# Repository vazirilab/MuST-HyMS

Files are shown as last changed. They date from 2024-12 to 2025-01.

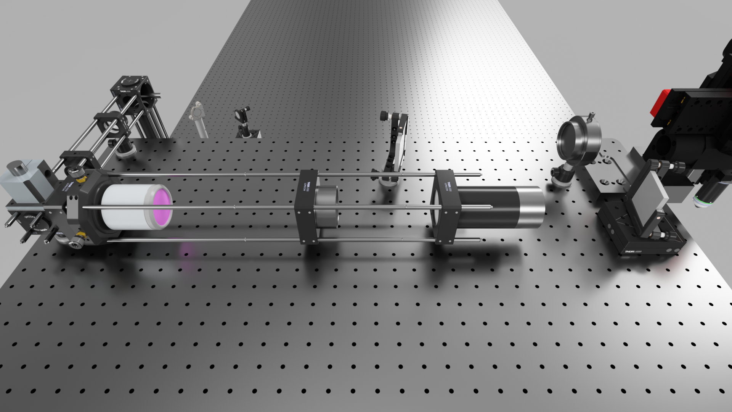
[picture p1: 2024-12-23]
Mechanical/03_3p-path_table-and-pltfrm/MuST_assembly_3p_v1_2017-Feb-16_03-30-20PM-000_CustomizedView4601048668.png

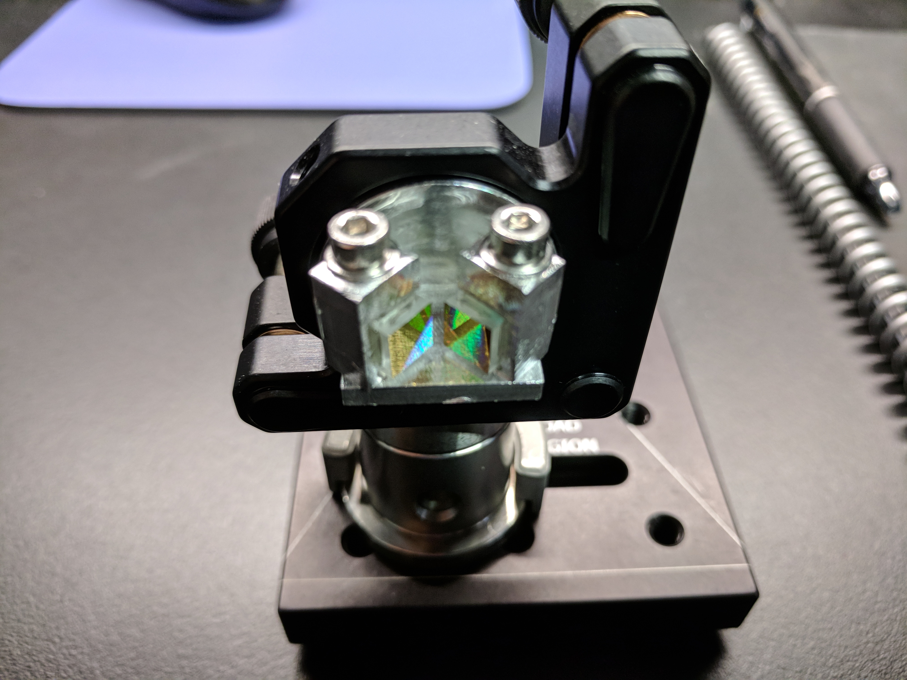
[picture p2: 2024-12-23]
Docs_Photos/HyMS_setup_photos/IMG_20180208_113904.jpg

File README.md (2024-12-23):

# Muliplexed Scanned Temporal Focusing (MuST) and Hybrid Multiplexed Sculpted Light (HyMS) Microscopy

This repository contains mechanical designs, parts lists, processing code, manuals, photos and other resources that enable users skilled in optical and mechanical lab techniques to build the MuST / HyMS microscope as published in the following peer-reviewed article:

Weisenburger, S., Tejera, F., Demas, J., Chen, B., Manley, J., Sparks, F. T., Martínez Traub, F., Daigle, T., Zeng, H., Losonczy, A. & Vaziri, A. 
Volumetric Ca<sup>2+</sup> Imaging in the Mouse Brain Using Hybrid Multiplexed Sculpted Light Microscopy. Cell 177, 1050-1066.e14 (2019). [doi:10.1016/j.cell.2019.03.011](https://doi.org/10.1016/j.cell.2019.03.011).

#### System requirements of the [MuST / HyMS processing pipeline](Code/)
- MATLAB Base
- MATLAB Parallel Computing Toolbox
- MATLAB Image Processing Toolbox
- MATLAB Statistics and Machine Learning Toolbox
- [ScanImageTiffReader](https://vidriotech.gitlab.io/scanimage-tiff-reader/)
- [NoRMCorre](https://github.com/flatironinstitute/NoRMCorre)
- [CaImAn-MATLAB](https://github.com/flatironinstitute/CaImAn-MATLAB)
- Tested with MATLAB R2017b on Red Hat Enterprise Linux 7.2

For additional information, please refer to the [Scan-TeFo / MuST / HyMS dissemination wiki](https://scantefo.rockefeller.edu/index.php?title=Main_Page).

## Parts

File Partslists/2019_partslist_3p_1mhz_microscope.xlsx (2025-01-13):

Parts | Vendor | Description | Part number | Qty
Laser | Class-5 | Class-5, OPCPA, 1300 nm, 1 MHz | WD
HWP | Thorlab | WPMH05M-1310 - Ø1/2" Mounted Multi-Order Half-Wave Plate, Ø1" Mount, 1310 nm | WPMH05M-1310 | 1
PBS | Thorlab | PBS123 - 1/2" Polarizing Beamsplitter Cube, 900 - 1300 nm | PBS123 | 1
L1 | Thorlab | Ø1" N-BK7 Plano-Convex Lens, SM1-Threaded Mount, f = 150 mm, ARC: 1050-1700 nm | LA1433-C-ML | 1
L2 | Thorlab | N-BK7 Plano-Concave Lens, Ø25 mm, f = -75 mm, AR Coating: 1050-1700 nm | LC1258-C | 1
EOM | Conoptics | Electro optic modulator Model 360-80 | 360-80 | 1
P1,P2 | Newport | Brewster Angle Dispersing Prism, Ultrafast, SF10, 25 mm, 370-2000 nm | 10SF10 | 2
Md | Thorlab | PFD10-03-P01 - Ø1" Protected Silver D-Shaped Mirror | PFD10-03-P01 | 1
M1 | Thorlab | PFSQ20-03-P01 - 2" x 2" Protected Silver Mirror | PFSQ20-03 | 1
M | Thorlab | PF10-03-P01 - Ø1" Protected Silver Mirror | PF10-03-P01 | 5
BS | Thorlab | Ø1/2" UVFS Beam Sampler for Beam Pick-Off, ARC: 1050-1700 nm, 3 mm Thick | BSF05-C | 1
PD | Thorlab | InGaAs Switchable Gain Amplified Detector, 800 - 1700 nm, 10 MHz BW, 3.14 mm2, M4 Taps | PDA20CS-EC | 1
L3,L4 | Thorlab | Mounted N-BK7 Bi-Convex Lens, Ø1", f = 125.0 mm, ARC: 1050 - 1700 nm | LB1904-C-ML | 2
L5, L6 | Thorlab | N-BK7 Plano-Convex Lens, Ø1", f = 100 mm, AR Coating: 1050 - 1700 nm | LA1509-C | 2
Rx | EOPC | 3 mm resonance scanner, 16 KHz | SC30 | 1
GX,Gy | Cambridge Tech | 5 mm Galvo scanner X and Y | 6215H | 1
SL | Thorlab | LSM05 - Scan Lens, 1250 to 1380 nm, EFL=110 mm | LSM05 | 1
S | Thorlab | SH1/M - Optical Beam Shutter with 10' Long Cable, Ø1" Aperture, Metric | SH1/M | 1
TL | Edmund Optics | f 400 mm achromactic lens |  | 1
OL | Nikon | Nikon 16x, 0.8 NA, 3 mm WD | CFI75LWD16xW2 | 1
Microscope Head | Sutter | Three axis movable objective microscope, 21.5 mm travel range | MP285 | 1
Microscope Optics | Semrock | 735 nm long pass dichroic mirror, 25 x 36 mm | FF735-Di02-25x36 | 1
 | Chroma | 575 nm longpass filter | 565DCXR | 1
 | Chroma | 605 nm bandpass filter | ET605/70m | 1
 | Chroma | 525 nm bandpass filter | ET525/70m | 1
PMT | Hamamatsu | Hamamatsu PMTs. GaAsP photocathode | H10770PA-40 | 2

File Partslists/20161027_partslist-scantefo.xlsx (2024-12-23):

Category | Purpose | Vendor | Part Number | Item | Product URL | Qty | Price | Subtotal | Currency | Order? | Arrived?
Multiplexing | 2x multiplexing | Thorlabs | PBS103 | 10 mm Polarizing Beamsplitter Cube 900 - 1300 nm | http://www.thorlabs.com/newgrouppage9.cfm?objectgroup_id=739 | 2 | $164.70 | $329.40 | USD | order by 30/05/2016 | YES
Multiplexing | 2x multiplexing | Thorlabs | AHWP05M-980 | Ø1/2" Mounted Achromatic Half-Wave Plate Ø1" Mount 690 - 1200 nm | http://www.thorlabs.com/newgrouppage9.cfm?objectgroup_id=854 | 1 | $704.70 | $704.70 | USD | order by 30/05/2016 | YES
Multiplexing | 2x multiplexing | Thorlabs | RSP1/M | Rotation Mount for Ø1" (25.4 mm) Optics M4 Tap | http://www.thorlabs.com/newgrouppage9.cfm?objectgroup_id=246 | 1 | $74.45 | $74.45 | USD | order by 30/05/2016 | YES
Multiplexing | 2x multiplexing | Thorlabs | MRA10-E03 | Right-Angle Prism Dielectric Mirror 750 - 1100 nm L = 10.0 mm | http://www.thorlabs.com/newgrouppage9.cfm?objectgroup_id=7715 | 1 | $94.50 | $94.50 | USD | order by 30/05/2016 | YES
Multiplexing | 2x multiplexing | Thorlabs | KM200S | Kinematic Mount for 2" (50.8 mm) Tall Rectangular Optics Right Handed | http://www.thorlabs.com/newgrouppage9.cfm?objectgroup_id=3971 | 2 | $119.70 | $239.40 | USD | order by 30/05/2016 | YES
Multiplexing | 2x multiplexing | Thorlabs | BBSQ2-E03 | 2" x 2" Square Broadband Dielectric Mirror 750 - 1100 nm | http://www.thorlabs.com/newgrouppage9.cfm?objectgroup_id=139 | 2 | $146.52 | $293.04 | USD | order by 30/05/2016 | YES
Multiplexing | 2x multiplexing | Thorlabs | PFD10-03-P01 | 1" Protected Silver D-Shaped Mirror | http://www.thorlabs.com/newgrouppage9.cfm?objectgroup_id=2632 | 2 | $49.50 | $99.00 | USD | order by 30/05/2016 | YES
Multiplexing | 2x multiplexing | Thorlabs | KM100D | Right-Handed Kinematic Mount for Ø1" D-Shaped Mirrors | http://www.thorlabs.com/newgrouppage9.cfm?objectgroup_id=2700 | 1 | $68.13 | $68.13 | USD | order by 30/05/2016 | YES
Multiplexing | 2x multiplexing | Thorlabs | BS011 | 50:50 Non-Polarizing Beamsplitter Cube 700-1100 nm 10 mm | http://www.thorlabs.com/newgrouppage9.cfm?objectgroup_id=6207 | 2 | $152.10 | $304.20 | USD | order by 30/05/2016 | YES
Multiplexing | 2x multiplexing | Thorlabs | MT1/M | 13 mm Translation Stage with Standard Micrometer M6 Taps | http://www.thorlabs.com/newgrouppage9.cfm?objectgroup_id=1908 | 2 | $257.40 | $514.80 | USD | order by 30/05/2016 | YES
Multiplexing | 2x multiplexing | Thorlabs | LMR3/M | Lens Mount with Retaining Ring for Ø3" Optics M4 Tap | http://www.thorlabs.com/newgrouppage9.cfm?objectgroup_id=1433 | 1 | $46.31 | $46.31 | USD | order by 30/05/2016 | YES
Multiplexing | 2x multiplexing | Thorlabs | KM100PM/M | 25 mm Kinematic Prism Mount M4 Taps | http://www.thorlabs.com/newgrouppage9.cfm?objectgroup_id=1811 | 5 | $65.25 | $326.25 | USD | order by 30/05/2016 | YES
Multiplexing | 2x multiplexing | Thorlabs | TR75/M | Ø12.7 mm Optical Post SS M4 Setscrew M6 Tap L = 75 mm | http://www.thorlabs.com/newgrouppage9.cfm?objectgroup_id=1266 | 7 | $4.88 | $34.16 | USD | order by 30/05/2016 | YES
Multiplexing | 2x multiplexing | Thorlabs | UPH75/M | Ø12.7 mm Universal Post Holder Spring-Loaded Locking Thumbscrew L = 75 mm | http://www.thorlabs.com/newgrouppage9.cfm?objectgroup_id=1982 | 7 | $27.54 | $192.78 | USD | order by 30/05/2016 | YES
Multiplexing | 2x multiplexing | Thorlabs | ID25/M | Mounted Standard Iris 25 mm Max Aperture Metric | http://www.thorlabs.com/newgrouppage9.cfm?objectgroup_id=206 | 5 | $49.59 | $247.95 | USD | order by 30/05/2016 | YES
Multiplexing | 2x multiplexing | Thorlabs | MB60120/M | Aluminum Breadboard 600 mm x 1200 mm x 12.7 mm M6 Taps | http://www.thorlabs.com/newgrouppage9.cfm?objectgroup_id=159 | 1 | $805.50 | $805.50 | USD | order by 30/05/2016 | YES
Multiplexing | Electrooptical lens | Edmund | Stock #83-922 | Low Dispersion, NIR Coated, Electrically Focus-Tunable Lens | http://www.edmundoptics.com/optics/optical-lenses/specialty-lenses/electrically-focus-tunable-lenses/83922/ | 2 | €440.00 | €880.00 | EUR | Have | YES
Multiplexing | Electrooptical lens | Edmund | Stock #87-590 | Optotune Electrical Lens Driver | http://www.edmundoptics.com/optics/optical-lenses/specialty-lenses/optotune-electrical-lens-driver/87590/ | 2 | €195.00 | €390.00 | EUR | Have | YES
Multiplexing Total |  |  |  |  |  |  |  | €5644.57
Scan-TeFo | 2D Galvo | Thorlabs | GVSM002/M | 2D Galvo System with Metric Accessories | https://www.thorlabs.de/newgrouppage9.cfm?objectgroup_id=3770 | 1 | $2431.00 | $2431.00 | USD | order by 30/05/2016 | YES
Scan-TeFo | 2D Galvo | Thorlabs | GCM002/M | 2D Galvo 30 mm Cage System Mount Metric | https://www.thorlabs.de/newgrouppage9.cfm?objectgroup_id=3770 | 1 | $120.00 | $120.00 | USD | order by 30/05/2016 | YES
Scan-TeFo | 2D Galvo | Thorlabs | CXY2 | 60 mm Cage System Translating Lens Mount for Ø2" Optics | https://www.thorlabs.de/newgrouppage9.cfm?objectgroup_id=4118 | 2 | $185.00 | $370.00 | USD | order by 30/05/2016 | YES
Scan-TeFo | 2D Galvo | Thorlabs | LCP02/M | 30 mm to 60 mm Cage Plate Adapter M4 Tap | https://www.thorlabs.de/newgrouppage9.cfm?objectgroup_id=1750 | 1 | $38.00 | $38.00 | USD | order by 30/05/2016 | YES
Scan-TeFo | 2D Galvo | Thorlabs | ER8-P4 | Cage Assembly Rod 8" (203.2 mm) Long Ø6 mm 4 Pack | https://www.thorlabs.de/newgrouppage9.cfm?objectgroup_id=4125 | 2 | $43.47 | $86.94 | USD | order by 30/05/2016 | YES
Scan-TeFo | 2D Galvo | Thorlabs | ER4-P4 | Cage Assembly Rod 4" (101.6 mm) Long Ø6 mm 4 Pack | https://www.thorlabs.de/newgrouppage9.cfm?objectgroup_id=4125 | 2 | $26.37 | $52.74 | USD | order by 30/05/2016 | YES
Scan-TeFo | 2D Galvo | Thorlabs | ER2-P4 | Cage Assembly Rod 2" (50.8 mm) Long Ø6 mm 4 Pack | https://www.thorlabs.de/newgrouppage9.cfm?objectgroup_id=4125 | 2 | $22.57 | $45.14 | USD | order by 30/05/2016 | YES
Scan-TeFo | 2D Galvo | Thorlabs | LSM03-BB | 5X OCT Scan Lens EFL=36 mm Design Wavelengths: 850 & 1050 nm | https://www.thorlabs.de/newgrouppage9.cfm?objectgroup_id=2910 | 1 | $979.00 | $979.00 | USD | order by 30/05/2016 | YES
Scan-TeFo | 2D Galvo | Thorlabs | BE02-05-B | Optical Beam Expander 2X - 5X Zoom AR Coated: 650 - 1050 nm | https://www.thorlabs.de/newgrouppage9.cfm?objectgroup_id=3211 | 1 | $1155.00 | $1155.00 | USD | order by 30/05/2016 | YES
Scan-TeFo | Beam delivery and control | Thorlabs | LA4874-B | f=150 mm Ø1" UVFS Plano-Convex Lens ARC: 650 - 1050 nm | https://www.thorlabs.de/newgrouppage9.cfm?objectgroup_id=6532 | 1 | $95.40 | $95.40 | USD | ORDER by 27/10/2016 | YES
Scan-TeFo | Beam delivery and control | Thorlabs | LC4513-B | Ø1" f = -75mm UV Fused Silica Plano-Concave Lens ARC: 650 - 1050 nm | https://www.thorlabs.de/newgrouppage9.cfm?objectgroup_id=6502 | 1 | $91.30 | $91.30 | USD | ORDER by 27/10/2016 | YES
Scan-TeFo | Beam delivery and control | Thorlabs | BSF10-B | Ø1" UVFS Beam Sampler for Beam Pick-Off ARC: 650-1050 nm 5 mm Thick | https://www.thorlabs.de/newgrouppage9.cfm?objectgroup_id=913 | 1 | $61.30 | $61.30 | USD | order by 30/05/2016 | YES
Scan-TeFo | Beam delivery and control | Thorlabs | PDA36A | Si Switchable Gain Detector 350-1100 nm 10 MHz BW 13 mm<sup>2</sup> 120 VAC | https://www.thorlabs.de/newgrouppage9.cfm?objectgroup_id=3257 | 1 | $314.00 | $314.00 | USD | order by 30/05/2016 | YES
Scan-TeFo | Beam delivery and control | Thorlabs | LDS1212 | ±12 VDC Regulated Linear Power Supply 6 W 115/230 VAC | https://www.thorlabs.de/newgrouppage9.cfm?objectgroup_id=8861 | 1 | $77.00 | $77.00 | USD | order by 30/05/2016 | YES
Scan-TeFo | Beam delivery and control | Thorlabs | SH05/M | Optical Beam Shutter with 10' Long Cable Ø1/2" Aperture M4 Taps | https://www.thorlabs.de/newgrouppage9.cfm?objectgroup_id=927 | 1 | $451.00 | $451.00 | USD | order by 30/05/2016 | YES
Scan-TeFo | Beam delivery and control | Thorlabs | SC10 | Optical Beam Shutter Controller | https://www.thorlabs.de/newgrouppage9.cfm?objectgroup_id=927 | 1 | $710.00 | $710.00 | USD | order by 30/05/2016 | YES
Scan-TeFo | Beam delivery and control | Thorlabs | KCB1/M | Right-Angle Kinematic Mirror Mount with Tapped Cage Rod Holes 30 mm Cage System and SM1 Compatible M4 and M6 Mounting Holes | https://www.thorlabs.de/newgrouppage9.cfm?objectgroup_id=6813 | 2 | $139.94 | $279.88 | USD | order by 30/05/2016 | YES
Scan-TeFo | Beam delivery and control | Thorlabs | KCB1C/M | Right-Angle Kinematic Mirror Mount with Smooth Cage Rod Bores 30 mm Cage System and SM1 Compatible M4 and M6 Mounting Holes | https://www.thorlabs.de/newgrouppage9.cfm?objectgroup_id=6813 | 2 | $139.94 | $279.88 | USD | order by 30/05/2016 | YES
Scan-TeFo | Beam delivery and control | Thorlabs | MT1/M | 13 mm Translation Stage with Standard Micrometer M6 Taps | https://www.thorlabs.de/newgrouppage9.cfm?objectgroup_id=1908 | 2 | $286.00 | $572.00 | USD | order by 30/05/2016 | YES
Scan-TeFo | DAQ | ScanImage | n/a | ScanImage and National Instruments DAQ | see quote | 1 | $32156.30 | $32156.30 | USD | order by 01/09/2016 | YES
Scan-TeFo | DAQ | Edmund | #59-179 | Variable High Speed Current Amplifier | http://www.edmundoptics.com/testing-detection/amplifiers/high-speed-current-amplifier/59179/ | 2 | $3150.00 | $6300.00 | USD | order by 30/05/2016 | YES
Scan-TeFo | General | Thorlabs | SM1D12 | SM1 Lever-Actuated Iris Diaphragm (Ø0.8 - Ø12 mm) | https://www.thorlabs.com/thorproduct.cfm?partnumber=SM1D12 | 2 | $55.70 | $111.40 | USD | ORDER by 27/10/2016 | YES
Scan-TeFo | General | Thorlabs | SM1L40 | SM1 Lens Tube, 4.00" Thread Depth, One Retaining Ring Included | https://www.thorlabs.com/thorproduct.cfm?partnumber=SM1L40 | 2 | $44.00 | $88.00 | USD | ORDER by 27/10/2016 | YES
Scan-TeFo | General | Thorlabs | WG11010-B | Ø1" N-BK7 Broadband Precision Window, AR Coated: 650 - 1050 nm, t = 1 mm | https://www.thorlabs.com/thorproduct.cfm?partnumber=WG11010-B | 2 | $85.00 | $170.00 | USD | ORDER by 27/10/2016 | YES
Scan-TeFo | General | Thorlabs | SM1A2 | Adapter with External SM1 Threads and Internal SM2 Threads | https://www.thorlabs.com/thorproduct.cfm?partnumber=SM1A2 | 1 | $24.00 | $24.00 | USD | ORDER by 27/10/2016 | YES
Scan-TeFo | General | Thorlabs | LCP01/M | 60 mm Cage Plate, SM2 Threads, 0.5" Thick, M4 Tap (Two SM2RR Retaining Rings Included) | https://www.thorlabs.com/thorproduct.cfm?partnumber=LCP01/M | 3 | $37.10 | $111.30 | USD | ORDER by 27/10/2016 | YES
Scan-TeFo | General | Thorlabs | LCP01T/M | 60 mm Cage Plate, SM2 Threads, 0.9" Thick, M4 Tap (Two SM2RR Retaining Rings Included) | https://www.thorlabs.com/thorproduct.cfm?partnumber=LCP01T/M | 1 | $36.60 | $36.60 | USD | ORDER by 27/10/2016 | YES
Scan-TeFo | General | Thorlabs | AC254-060-B-ML | f=60mm, Ø1" Achromatic Doublet, SM1-Threaded Mount, ARC: 650-1050 nm | https://www.thorlabs.com/thorproduct.cfm?partnumber=AC254-060-B-ML | 1 | $108.00 | $108.00 | USD | ORDER by 27/10/2016 | YES
Scan-TeFo | General | Thorlabs | ER8-P4 | Cage Assembly Rod, 8" Long, Ø6 mm, 4 Pack | https://www.thorlabs.com/thorproduct.cfm?partnumber=ER8-P4 | 1 | $43.47 | $43.47 | USD | ORDER by 27/10/2016 | YES
Scan-TeFo | General | Thorlabs | SM2L30 | SM2 Lens Tube, 3" Thread Depth, One Retaining Ring Included | https://www.thorlabs.com/thorproduct.cfm?partnumber=SM2L30 | 1 | $35.50 | $35.50 | USD | ORDER by 27/10/2016 | YES
Scan-TeFo | General | Thorlabs | SM3A2 | Adapter with External SM2 Threads and Internal SM3 Threads | https://www.thorlabs.com/thorproduct.cfm?partnumber=SM3A2 | 1 | $29.00 | $29.00 | USD | ORDER by 27/10/2016 | YES
Scan-TeFo | General | Thorlabs | SM3L20 | 2" SM3 Series Lens Tube | https://www.thorlabs.com/thorproduct.cfm?partnumber=SM3L20 | 1 | $42.00 | $42.00 | USD | ORDER by 27/10/2016 | YES
Scan-TeFo | General | Thorlabs | SM3L10 | SM3 Lens Tube 1" Thread Depth | https://www.thorlabs.com/thorproduct.cfm?partnumber=SM3L10 | 1 | $38.00 | $38.00 | USD | ORDER by 27/10/2016 | YES
Scan-TeFo | General | Thorlabs | AC508-500-B-ML | f=500 mm, Ø2" Achromatic Doublet, SM2-Threaded Mount, ARC: 650-1050 nm | https://www.thorlabs.com/thorproduct.cfm?partnumber=AC508-500-B-ML | 1 | $163.00 | $163.00 | USD | ORDER by 27/10/2016 | YES
Scan-TeFo | General | Thorlabs | SM1CP2M | Externally SM1-Threaded End Cap for Machining | https://www.thorlabs.com/thorproduct.cfm?partnumber=SM1CP2M | 2 | $18.00 | $36.00 | USD | ORDER by 27/10/2016 | YES
Scan-TeFo | General | Thorlabs | BBSQ2-E02 | 2" x 2" Square Broadband Dielectric Mirror, 400 - 750 nm | https://www.thorlabs.com/thorproduct.cfm?partnumber=BBSQ2-E02 | 1 | $162.80 | $162.80 | USD | ORDER by 27/10/2016 | YES
Scan-TeFo | General | Thorlabs | BB1-E03-10 | Ø1" Broadband Dielectric Mirrors 750 - 1100 nm 10 Pack | https://www.thorlabs.de/newgrouppage9.cfm?objectgroup_id=139 | 1 | $675.90 | $675.90 | USD | order by 30/05/2016 | YES
Scan-TeFo | General | Thorlabs | RS2P4M | Ø25.0 mm Pedestal Pillar Post M4 Taps L = 50 mm | https://www.thorlabs.de/newgrouppage9.cfm?objectgroup_id=851 | 5 | $23.50 | $117.50 | USD | order by 30/05/2016 | YES
Scan-TeFo | General | Thorlabs | RS05P4M | Ø25.0 mm Pedestal Pillar Post M4 Taps L = 12.5 mm | https://www.thorlabs.de/newgrouppage9.cfm?objectgroup_id=851 | 7 | $18.90 | $132.30 | USD | order by 30/05/2016 | YES
Scan-TeFo | General | Thorlabs | RS075P4M | Ø25.0 mm Pedestal Pillar Post M4 Taps L = 19 mm | https://www.thorlabs.de/newgrouppage9.cfm?objectgroup_id=851 | 7 | $20.50 | $143.50 | USD | order by 30/05/2016 | YES
Scan-TeFo | General | Thorlabs | RS1.5P4M | Ø25.0 mm Pedestal Pillar Post M4 Taps L = 38 mm | https://www.thorlabs.de/newgrouppage9.cfm?objectgroup_id=851 | 5 | $22.75 | $113.75 | USD | order by 30/05/2016 | YES
Scan-TeFo | General | Thorlabs | RS1P4M | Ø25.0 mm Pedestal Pillar Post M4 Taps L = 25 mm | https://www.thorlabs.de/newgrouppage9.cfm?objectgroup_id=851 | 7 | $21.00 | $147.00 | USD | order by 30/05/2016 | YES
Scan-TeFo | General | Thorlabs | TR75/M | Ø12.7 mm Optical Post SS M4 Setscrew M6 Tap L = 75 mm | https://www.thorlabs.de/newgrouppage9.cfm?objectgroup_id=1266 | 5 | $5.42 | $27.10 | USD | order by 30/05/2016 | YES
Scan-TeFo | General | Thorlabs | TR50/M | Ø12.7 mm Optical Post SS M4 Setscrew M6 Tap L = 50 mm | https://www.thorlabs.de/newgrouppage9.cfm?objectgroup_id=1266 | 5 | $5.19 | $25.95 | USD | order by 30/05/2016 | YES
Scan-TeFo | General | Thorlabs | TR40/M | Ø12.7 mm Optical Post SS M4 Setscrew M6 Tap L = 40 mm | https://www.thorlabs.de/newgrouppage9.cfm?objectgroup_id=1266 | 5 | $4.97 | $24.85 | USD | order by 30/05/2016 | YES
Scan-TeFo | General | Thorlabs | TR30/M | Ø12.7 mm Optical Post SS M4 Setscrew M6 Tap L = 30 mm | https://www.thorlabs.de/newgrouppage9.cfm?objectgroup_id=1266 | 5 | $4.74 | $23.70 | USD | order by 30/05/2016 | YES
Scan-TeFo | General | Thorlabs | TR20/M | Ø12.7 mm Optical Post SS M4 Setscrew M6 Tap L = 20 mm | https://www.thorlabs.de/newgrouppage9.cfm?objectgroup_id=1266 | 5 | $4.74 | $23.70 | USD | order by 30/05/2016 | YES
Scan-TeFo | General | Thorlabs | PH20/M-P5 | Ø12.7 mm Post Holders Spring-Loaded Hex-Locking Thumbscrew L=20 mm 5 Pack | https://www.thorlabs.de/newgrouppage9.cfm?objectgroup_id=1268 | 2 | $35.15 | $70.30 | USD | order by 30/05/2016 | YES
Scan-TeFo | General | Thorlabs | PH30/M-P5 | Ø12.7 mm Post Holders Spring-Loaded Hex-Locking Thumbscrew L=30 mm 5 Pack | https://www.thorlabs.de/newgrouppage9.cfm?objectgroup_id=1268 | 2 | $35.15 | $70.30 | USD | order by 30/05/2016 | YES
Scan-TeFo | General | Thorlabs | PH40/M-P5 | Ø12.7 mm Post Holders Spring-Loaded Hex-Locking Thumbscrew L=40 mm 5 Pack | https://www.thorlabs.de/newgrouppage9.cfm?objectgroup_id=1268 | 2 | $36.10 | $72.20 | USD | order by 30/05/2016 | YES
Scan-TeFo | General | Thorlabs | SM1A10 | Adapter with External SM1 Threads and Internal C-Mount Threads | https://www.thorlabs.de/newgrouppage9.cfm?objectgroup_id=1524 | 2 | $18.75 | $37.50 | USD | order by 30/05/2016 | YES
Scan-TeFo | General | Thorlabs | BE1/M | Ø31.8 mm Studded Pedestal Base Adapter M6 Thread | https://www.thorlabs.de/newgrouppage9.cfm?objectgroup_id=887 | 15 | $9.10 | $136.50 | USD | order by 30/05/2016 | YES
Scan-TeFo | General | Thorlabs | KM100 | Kinematic Mirror Mount for Ø1" Optics | https://www.thorlabs.de/newgrouppage9.cfm?objectgroup_id=1492 | 10 | $38.70 | $387.00 | USD | order by 30/05/2016 | YES
Scan-TeFo | General | Thorlabs | RM1A/M | Ø25.0 mm Post Clamp M4 Tap M4 Counterbore | https://www.thorlabs.de/newgrouppage9.cfm?objectgroup_id=2012 | 7 | $25.70 | $179.90 | USD | order by 30/05/2016 | YES
Scan-TeFo | General | Thorlabs | ID50/M | Mounted Standard Iris 50 mm Max Aperture Metric | https://www.thorlabs.de/newgrouppage9.cfm?objectgroup_id=206 | 3 | $117.00 | $351.00 | USD | order by 30/05/2016 | YES
Scan-TeFo | General | Thorlabs | ID25/M | Mounted Standard Iris 25 mm Max Aperture Metric | https://www.thorlabs.de/newgrouppage9.cfm?objectgroup_id=206 | 5 | $55.10 | $275.50 | USD | order by 30/05/2016 | YES
Scan-TeFo | General | Thorlabs | P300/M | Ø1.5" Mounting Post M6 Taps L = 300 mm | https://www.thorlabs.de/newgrouppage9.cfm?objectgroup_id=1313 | 4 | $79.00 | $316.00 | USD | order by 30/05/2016 | YES
Scan-TeFo | General | Thorlabs | P50/M | Ø1.5" Mounting Post M6 Taps L = 50 mm | https://www.thorlabs.de/newgrouppage9.cfm?objectgroup_id=1313 | 4 | $26.00 | $104.00 | USD | order by 30/05/2016 | YES
Scan-TeFo | General | Thorlabs | PF175 | Clamping Fork for Ø1.5" Pedestal Post or Post Pedestal Base Adapter Universal | https://www.thorlabs.de/newgrouppage9.cfm?objectgroup_id=887 | 4 | $17.47 | $69.88 | USD | order by 30/05/2016 | YES
Scan-TeFo | General | Thorlabs | MT1/M | 13 mm Translation Stage with Standard Micrometer M6 Taps | https://www.thorlabs.de/newgrouppage9.cfm?objectgroup_id=1908 | 2 | $286.00 | $572.00 | USD | order by 30/05/2016 | YES
Scan-TeFo | General | Thorlabs | PB4/M | Studded Pedestal Base Adapter M6 x 1.0 Thread | https://www.thorlabs.de/newgrouppage9.cfm?objectgroup_id=887 | 5 | $12.40 | $62.00 | USD | order by 30/05/2016 | YES
Scan-TeFo | General | Thorlabs | SM3T2 | SM3 (3.035"-40) Lens Tube Coupler External Threads | https://www.thorlabs.de/newgrouppage9.cfm?objectgroup_id=2704 | 1 | $37.10 | $37.10 | USD | order by 30/05/2016 | YES
Scan-TeFo | General | Thorlabs | SM2T2 | SM2 (2.035"-40) Coupler External Threads 1/2" Long | https://www.thorlabs.de/newgrouppage9.cfm?objectgroup_id=2704 | 1 | $34.00 | $34.00 | USD | order by 30/05/2016 | YES
Scan-TeFo | General | Thorlabs | ER4E | Engraved Cage Assembly Rod 4" (101.6 mm) Long Ø6 mm Qty. 1 | https://www.thorlabs.de/newgrouppage9.cfm?objectgroup_id=4125 | 1 | $15.50 | $15.50 | USD | order by 30/05/2016 | YES
Scan-TeFo | General | Thorlabs | ER6E | Engraved Cage Assembly Rod 6" (152.4 mm) Long Ø6 mm Qty. 1 | https://www.thorlabs.de/newgrouppage9.cfm?objectgroup_id=4125 | 1 | $15.50 | $15.50 | USD | order by 30/05/2016 | YES
Scan-TeFo | General | Thorlabs | ER2-P4 | Cage Assembly Rod 2" (50.8 mm) Long Ø6 mm 4 Pack | https://www.thorlabs.de/newgrouppage9.cfm?objectgroup_id=4125 | 2 | $22.57 | $45.14 | USD | order by 30/05/2016 | YES
Scan-TeFo | General | Thorlabs | ER3-P4 | Cage Assembly Rod 3" (76.2 mm) Long Ø6 mm 4 Pack | https://www.thorlabs.de/newgrouppage9.cfm?objectgroup_id=4125 | 2 | $24.47 | $48.94 | USD | order by 30/05/2016 | YES
Scan-TeFo | General | Thorlabs | ER4-P4 | Cage Assembly Rod 4" (101.6 mm) Long Ø6 mm 4 Pack | https://www.thorlabs.de/newgrouppage9.cfm?objectgroup_id=4125 | 2 | $26.37 | $52.74 | USD | order by 30/05/2016 | YES
Scan-TeFo | General | Thorlabs | ER6-P4 | Cage Assembly Rod 6" (152.4 mm) Long Ø6 mm 4 Pack | https://www.thorlabs.de/newgrouppage9.cfm?objectgroup_id=4125 | 1 | $31.42 | $31.42 | USD | order by 30/05/2016 | YES
Scan-TeFo | General | Thorlabs | ER05-P4 | Cage Assembly Rod 1/2" (12.7 mm) Long Ø6 mm 4 Pack | https://www.thorlabs.de/newgrouppage9.cfm?objectgroup_id=4125 | 1 | $18.77 | $18.77 | USD | order by 30/05/2016 | YES
Scan-TeFo | General | Thorlabs | ER1-P4 | Cage Assembly Rod 1" (25.4 mm) Long Ø6 mm 4 Pack | https://www.thorlabs.de/newgrouppage9.cfm?objectgroup_id=4125 | 1 | $18.77 | $18.77 | USD | order by 30/05/2016 | YES
Scan-TeFo | General | Thorlabs | ER12 | Cage Assembly Rod 12" (304.8 mm) Long Ø6 mm | https://www.thorlabs.de/newgrouppage9.cfm?objectgroup_id=4125 | 4 | $16.44 | $65.76 | USD | order by 30/05/2016 | YES
Scan-TeFo | General | Thorlabs | CPS532-C2 | Collimated Laser Diode Module 532 nm 0.9 mW Round Beam Ø11 mm Housing | https://www.thorlabs.de/newgrouppage9.cfm?objectgroup_id=1487 | 1 | $155.00 | $155.00 | USD | order by 30/05/2016 | YES
Scan-TeFo | General | Thorlabs | LDS5-EC | 5 VDC Regulated Power Supply 2.5 mm Phono Plug 230 VAC | https://www.thorlabs.de/newgrouppage9.cfm?objectgroup_id=8861 | 1 | $83.35 | $83.35 | USD | order by 30/05/2016 | YES
Scan-TeFo | General | Thorlabs | AD11F | SM1-Threaded Adapter for Ø11 mm Cylindrical Components | https://www.thorlabs.de/newgrouppage9.cfm?objectgroup_id=219 | 1 | $27.80 | $27.80 | USD | order by 30/05/2016 | YES
Scan-TeFo | General | Thorlabs | VRC2D1 | Ø1" VIS and IR Alignment Disk (400 - 640 800 - 1700 nm) | https://www.thorlabs.de/newgrouppage9.cfm?objectgroup_id=3201 | 1 | $33.50 | $33.50 | USD | order by 30/05/2016 | YES
Scan-TeFo | General | Thorlabs | VRC2RMS | RMS-Threaded VIS and IR Alignment Disk (400-640 nm 800-1700 nm) | https://www.thorlabs.de/newgrouppage9.cfm?objectgroup_id=3201 | 1 | $82.40 | $82.40 | USD | order by 30/05/2016 | YES
Scan-TeFo | General | Thorlabs | VRC2SM1 | SM1-Threaded VIS and IR Alignment Disk (400-640 nm 800-1700 nm) | https://www.thorlabs.de/newgrouppage9.cfm?objectgroup_id=3201 | 1 | $78.80 | $78.80 | USD | order by 30/05/2016 | YES
Scan-TeFo | General | Thorlabs | T4290 | SMA Male to BNC Female Adapter | https://www.thorlabs.de/newgrouppage9.cfm?objectgroup_id=289 | 5 | $12.70 | $63.50 | USD | order by 30/05/2016 | YES
Scan-TeFo | General | Thorlabs | T3533 | BNC Adapter - Straight Adapter (M-M) | https://www.thorlabs.de/newgrouppage9.cfm?objectgroup_id=289 | 5 | $12.70 | $63.50 | USD | order by 30/05/2016 | YES
Scan-TeFo | General | Thorlabs | VRC4 | IR Detector Card 790 - 840 nm 870 - 1070 nm 1500 - 1590 nm | https://www.thorlabs.de/newgrouppage9.cfm?objectgroup_id=296 | 1 | $79.00 | $79.00 | USD | order by 30/05/2016 | YES
Scan-TeFo | General | Thorlabs | VRC2 | VIS/IR Detector Card 400 - 640 nm 800 - 1700 nm | https://www.thorlabs.de/newgrouppage9.cfm?objectgroup_id=296 | 1 | $79.00 | $79.00 | USD | order by 30/05/2016 | YES
Scan-TeFo | General | Thorlabs | P350/M | Ø1.5" Mounting Post M6 Taps L = 350 mm | https://www.thorlabs.de/newgrouppage9.cfm?objectgroup_id=1313 | 1 | $88.00 | $88.00 | USD | order by 30/05/2016 | YES
Scan-TeFo | General | Newport | M-TD-23 | Composite Core Optical Breadboard, 600 x 900 x 28 mm, M6 Holes | http://search.newport.com/?q=*&x2=sku&q2=M-TD-23 | 1 | $654.00 | $654.00 | USD | order by 30/05/2016 | YES
Scan-TeFo | Laser source | Active Fiber Lasers | UFFL | 2 channel fiber laser, 50W and 10W, 1035nm, 350fs | see quote | 1 | €147000.00 | €147000.00 | EUR | Have | YES
Scan-TeFo | Microscope | Chroma | n/a | Optical filters | see quote | 1 | $2525.00 | $2525.00 | USD | order by 30/05/2016 | YES
Scan-TeFo | Microscope | AHF | F76-705 | Multiphoton beamsplitter | see quote - ONLY ITEM #1 in the quote | 1 | €559.55 | €559.55 | EUR | order by 30/05/2016 | YES
Scan-TeFo | Microscope | Edmund | #89-458 | Elliptical Mirror 38.1mm Minor Axis Protected Silver | http://www.edmundoptics.com/optics/optical-mirrors/flat-mirrors/precision-elliptical-flat-mirrors/89458/ | 1 | $115.00 | €115.00 | USD | order by 30/05/2016 | YES
Scan-TeFo | Microscope | Sutter | MP-285 | Microscope stage and detectors | see quote | 1 | $44216.60 | $44216.60 | USD | order by 30/05/2016 | YES
Scan-TeFo | Microscope | Edmund | #49-284 | 50mm Dia. x 100mm FL, VIS 0° Coated, Achromatic Lens | http://www.edmundoptics.com/optics/optical-lenses/achromatic-lenses/vis-0-coated-achromatic-lenses/49284/ | 1 | $140.00 | $140.00 | USD | order by 30/05/2016 | YES
Scan-TeFo | Microscope | Newport | KPA034-C | Aspheric Condenser Lens, 32.5 mm Diameter, 23 mm EFL, 400-700 nm | http://search.newport.com/?q=*&x2=sku&q2=KPA034-C | 2 | $70.00 | $140.00 | USD | order by 30/05/2016 | YES
Scan-TeFo | Microscope | Thorlabs | N16XLWD-PF | 16X Nikon CFI LWD Plan Fluorite Objective 0.80 NA 3.0 mm WD | https://www.thorlabs.de/newgrouppage9.cfm?objectgroup_id=5824 | 1 | $5824.21 | $5824.21 | USD | order by 30/05/2016 | YES
Scan-TeFo | Microscope | Thorlabs | M32A1 | Adapter with External M32 x 0.75 Threads and Internal M25 x 0.75 Threads | https://www.thorlabs.de/newgrouppage9.cfm?objectgroup_id=1834 | 1 | $21.56 | $21.56 | USD | order by 30/05/2016 | YES
Scan-TeFo | Objective piezo | Npoint | - | NPFocus 1000 + LC400 DSP Controller | see quote | 1 | $12699.00 | $12699.00 | USD | Have | YES
Scan-TeFo | Polygonal scanner | LincolnLaser | MPA DT72-250 | Polygonal scanner | see quote | 1 | $3811.00 | $3811.00 | USD | N
Scan-TeFo | Remote scanning | Akribis Sys | n/a | n/a | see quote | 1 | $2500.00 | $2500.00 | USD | N
Scan-TeFo | Pockel's cell | ConOptics | 350-80-LA-02 | EOM | see quote | 1 | $10215.00 | $10215.00 | USD | Have | YES
Scan-TeFo | Resonant galvo | EOPC | - | 16kHz resonant mirror | see quote | 1 | $1505.00 | $1505.00 | USD | Have | YES
Scan-TeFo | Scan relay | Edmund | #49-359-INK | 25mm Dia. x 85mm FL, VIS-NIR, Inked, Achromatic Lens | http://www.edmundoptics.com/optics/optical-lenses/achromatic-lenses/vis-nir-coated-achromatic-lenses/49359INK/ | 2 | $103.00 | $206.00 | USD | order by 30/05/2016 | YES
Scan-TeFo | Scan relay | Thorlabs | C6W | 30 mm Cage Cube Ø6 mm Through Holes | https://www.thorlabs.de/newgrouppage9.cfm?objectgroup_id=3929 | 2 | $61.20 | $122.40 | USD | order by 30/05/2016 | YES
Scan-TeFo | Scan relay | Thorlabs | CP02T/M | SM1-Threaded 30 mm Cage Plate 0.5" Thick 2 Retaining Rings M4 Tap | https://www.thorlabs.de/newgrouppage9.cfm?objectgroup_id=2273 | 4 | $21.00 | $84.00 | USD | order by 30/05/2016 | YES
Scan-TeFo | Scan relay | Thorlabs | CP06/M | Post-Mountable Cage Plate with Ø1.0" Double Bore M4 Tap | https://www.thorlabs.de/newgrouppage9.cfm?objectgroup_id=2273 | 2 | $16.75 | $33.50 | USD | order by 30/05/2016 | YES
Scan-TeFo | Scan relay | Thorlabs | SM1B3 | SM1 Lens Tube Bellows 1.50" to 8.66" Long | https://www.thorlabs.de/newgrouppage9.cfm?objectgroup_id=3394 | 2 | $45.00 | $90.00 | USD | order by 30/05/2016 | YES
Scan-TeFo | Scan relay | Thorlabs | ER12 | Cage Assembly Rod 12" (304.8 mm) Long Ø6 mm | https://www.thorlabs.de/newgrouppage9.cfm?objectgroup_id=4125 | 4 | $16.44 | $65.76 | USD | order by 30/05/2016 | YES
Scan-TeFo | Scan relay | Thorlabs | SM1L05 | SM1 Lens Tube 0.50" Thread Depth One Retaining Ring Included | https://www.thorlabs.de/newgrouppage9.cfm?objectgroup_id=3307 | 3 | $12.59 | $37.77 | USD | order by 30/05/2016 | YES
Scan-TeFo | Scan relay | Thorlabs | SM1L10 | SM1 Lens Tube 1.00" Thread Depth One Retaining Ring Included | https://www.thorlabs.de/newgrouppage9.cfm?objectgroup_id=3307 | 3 | $14.25 | $42.75 | USD | order by 30/05/2016 | YES
Scan-TeFo | Scan relay | Thorlabs | AC508-100-B-ML | f=100 mm Ø2" Achromatic Doublet SM2-Threaded Mount ARC: 650-1050 nm | https://www.thorlabs.de/newgrouppage9.cfm?objectgroup_id=3647 | 2 | $163.00 | $326.00 | USD | order by 30/05/2016 | YES
Scan-TeFo | Scan relay | Thorlabs | AC508-200-B-ML | f=200 mm Ø2" Achromatic Doublet SM2-Threaded Mount ARC: 650-1050 nm | https://www.thorlabs.de/newgrouppage9.cfm?objectgroup_id=3647 | 1 | $163.00 | $163.00 | USD | order by 30/05/2016 | YES
Scan-TeFo | Scan relay | Thorlabs | LE1929-B | Ø1" N-BK7 Positive Meniscus Lens f = 300 mm ARC: 650 - 1050 nm | https://www.thorlabs.de/newgrouppage9.cfm?objectgroup_id=130 | 2 | $32.81 | $65.62 | USD | order by 30/05/2016 | YES
Scan-TeFo | Scan relay | Thorlabs | CXY2 | 60 mm Cage System Translating Lens Mount for Ø2" Optics | https://www.thorlabs.de/newgrouppage9.cfm?objectgroup_id=4118 | 2 | $185.00 | $370.00 | USD | order by 30/05/2016 | YES
Scan-TeFo | Scan relay | Thorlabs | LSM05-BB | 1.6X OCT Scan Lens EFL=110 mm Design Wavelengths: 850 & 1050 nm | https://www.thorlabs.de/newgrouppage9.cfm?objectgroup_id=2910 | 1 | $969.00 | $969.00 | USD | order by 30/05/2016 | YES
Scan-TeFo | Scan relay | Thorlabs | LCP02/M | 30 mm to 60 mm Cage Plate Adapter M4 Tap | https://www.thorlabs.de/newgrouppage9.cfm?objectgroup_id=1750 | 2 | $38.00 | $76.00 | USD | order by 30/05/2016 | YES
Scan-TeFo | Scan relay | Thorlabs | B1C/M | Blank Cover Plate with Rubber O-Ring for C4W/C6W Metric | https://www.thorlabs.de/newgrouppage9.cfm?objectgroup_id=6858 | 4 | $18.00 | $72.00 | USD | order by 30/05/2016 | YES
Scan-TeFo | Scan relay | Thorlabs | SM1CP2M | Externally SM1-Threaded End Cap for Machining | https://www.thorlabs.de/newgrouppage9.cfm?objectgroup_id=3519 | 4 | $18.00 | $72.00 | USD | order by 30/05/2016 | YES
Scan-TeFo | Scan relay | Thorlabs | WG11010-B | Ø1" N-BK7 Broadband Precision Window AR Coated: 650 - 1050&nbsp;nm t = 1 mm | https://www.thorlabs.de/newgrouppage9.cfm?objectgroup_id=1117 | 2 | $85.00 | $170.00 | USD | order by 30/05/2016 | YES
Scan-TeFo | Scan relay | Thorlabs | SM1L03 | SM1 Lens Tube 0.30" Thread Depth One Retaining Ring Included | https://www.thorlabs.de/newgrouppage9.cfm?objectgroup_id=3307 | 4 | $12.16 | $48.64 | USD | order by 30/05/2016 | YES
Scan-TeFo | Temporal focusing | Edmund | #88-596 | 75mm Dia. x 200mm FL, VIS-NIR Coated, Achromatic Lens | http://www.edmundoptics.com/optics/optical-lenses/achromatic-lenses/vis-nir-coated-achromatic-lenses/88598/ | 1 | $275.00 | $275.00 | USD | ORDER by 27/10/2016 | YES
Scan-TeFo | Temporal focusing | Thorlabs | KB75/M | Complete 75 mm x 75 mm Kinematic Base Top and Bottom Plates M6 Mounting | https://www.thorlabs.de/newgrouppage9.cfm?objectgroup_id=1546 | 1 | $90.40 | $90.40 | USD | order by 30/05/2016 | YES
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

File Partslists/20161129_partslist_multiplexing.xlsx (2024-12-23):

Category | Purpose | Vendor | Part Number | Item | Product URL | Qty | Price | Subtotal | Currency | Order? | Arrived? | Comments
Multiplexing | 4x multiplexing | Thorlabs | PBS103 | 10 mm Polarizing Beamsplitter Cube 900 - 1300 nm | http://www.thorlabs.com/newgrouppage9.cfm?objectgroup_id=739 | 1 | $164.70 | $164.70 | USD | Have 2, need 3
Multiplexing | 4x multiplexing | Thorlabs | AHWP05M-980 | Ø1/2" Mounted Achromatic Half-Wave Plate Ø1" Mount 690 - 1200 nm | http://www.thorlabs.com/newgrouppage9.cfm?objectgroup_id=854 | 2 | $704.70 | $1409.40 | USD | Have 1, need 3
Multiplexing | 4x multiplexing | Thorlabs | RSP1/M | Rotation Mount for Ø1" (25.4 mm) Optics, M4 Tap | https://www.thorlabs.com/thorproduct.cfm?partnumber=RSP1/M | 2 | $82.72 | $165.44 | USD | Have 1, need 3
Multiplexing | 4x multiplexing | Thorlabs | PFD10-03-P01 | 1" Protected Silver D-Shaped Mirror | http://www.thorlabs.com/newgrouppage9.cfm?objectgroup_id=2632 | 1 | $49.50 | $49.50 | USD | Have 2, need 3
Multiplexing | 4x multiplexing | Thorlabs | KM100D | Right-Handed Kinematic Mount for Ø1" D-Shaped Mirrors | http://www.thorlabs.com/newgrouppage9.cfm?objectgroup_id=2700 | 2 | $68.13 | $136.26 | USD | Have 1, need 3
Multiplexing | 4x multiplexing | Thorlabs | PFSQ20-03-P01 | 2" x 2" (50.8 mm x 50.8 mm) Protected Silver Mirror, 0.24" (6 mm) Thick | https://www.thorlabs.com/newgrouppage9.cfm?objectgroup_id=903 | 3 | $111.00 | $333.00 | USD | Need 3
Multiplexing | 4x multiplexing | Thorlabs | KM200S | Kinematic Mount for 2" (50.8 mm) Tall Rectangular Optics Right Handed | http://www.thorlabs.com/newgrouppage9.cfm?objectgroup_id=3971 | 0 | $119.70 | $0.00 | USD | Have | YES
Multiplexing | 4x multiplexing | Thorlabs | POLARIS-19S-CUSTOM | Custom POLARIS Fixed 19mm Side Mount, Height: 120 mm, Mounting: M6, Dowel Pin: None, Include 6 mm Alignment Hole: No | https://www.thorlabs.com/newgrouppage9.cfm?objectgroup_id=8067&quickConfig=130_mm_M6__nobore_2qc&pn=POLARIS-19S-CUSTOM | 3 | $105.92 | $317.76 | USD | Need 3
Multiplexing | 4x multiplexing | Thorlabs | LA4874-B | f=150 mm Ø1" UVFS Plano-Convex Lens ARC: 650 - 1050 nm | https://www.thorlabs.de/newgrouppage9.cfm?objectgroup_id=6532 | 1 | $95.40 | $95.40 | USD | Need 1
Multiplexing | 4x multiplexing | Thorlabs | LC4513-B | Ø1" f = -75mm UV Fused Silica Plano-Concave Lens ARC: 650 - 1050 nm | https://www.thorlabs.de/newgrouppage9.cfm?objectgroup_id=6502 | 2 | $91.30 | $182.60 | USD | Need 2 |  | Other 2 lenses TBD
Multiplexing | 4x multiplexing | Thorlabs | PF07-03-P01 | Ø19.0 mm Protected Silver Mirror, 0.24" (6.0 mm) Thick | https://www.thorlabs.com/newgrouppage9.cfm?objectgroup_id=903&pn=PF07-03-P01 | 3 | $42.00 | $126.00 | USD | Need 3
Multiplexing | 4x multiplexing | Thorlabs | POLARIS-K1-2AH | Polaris™ Low Drift Ø1" Mirror Mount, 2 Low-Profile Hex Adjusters | https://www.thorlabs.com/newgrouppage9.cfm?objectgroup_id=3912 | 6 | $123.00 | $738.00 | USD | Need 6
Multiplexing | Electrooptical lens | Edmund | Stock #83-922 | Low Dispersion, NIR Coated, Electrically Focus-Tunable Lens | http://www.edmundoptics.com/optics/optical-lenses/specialty-lenses/electrically-focus-tunable-lenses/83922/ | 1 | €440.00 | $440.00 | EUR | Have 2, need 3 |  | Later
Multiplexing | Electrooptical lens | Edmund | Stock #87-590 | Optotune Electrical Lens Driver | http://www.edmundoptics.com/optics/optical-lenses/specialty-lenses/optotune-electrical-lens-driver/87590/ | 1 | €195.00 | $195.00 | EUR | Have 2, need 3 |  | Later
Multiplexing | 4x multiplexing | Thorlabs | UM10-AG | Ø1" Ultrafast-Enhanced Silver Mirror, 750 - 1000 nm | https://www.thorlabs.com/thorproduct.cfm?partnumber=UM10-AG | 12 | $95.00 | $1140.00 | USD | Need >12
 |  |  |  |  |  |  | Total | $5493.06 | USD

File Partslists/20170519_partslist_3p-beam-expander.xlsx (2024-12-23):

Category | Purpose | Vendor | Part Number | Item | Product URL | Qty | Price | Subtotal | Currency | Order? | Arrived? | Comments
3p path | Beam expander | Thorlabs | LC4513-C | LC4513-C - Ø1", f = -75 mm, UV Fused Silica Plano-Concave Lens, ARC: 1050 - 1700 nm | https://www.thorlabs.com/thorproduct.cfm?partnumber=LC4513-C | 2 | $96.50 | $193.00 | USD
3p path | Beam expander | Thorlabs | LA4874-C-ML | LA4874-C-ML - Ø1" UVFS Plano-Convex Lens, SM1-Threaded Mount, f = 150.0 mm, ARC: 1050 - 1700 nm | https://www.thorlabs.com/thorproduct.cfm?partnumber=LA4874-C-ML | 2 | $113.00 | $226.00 | USD

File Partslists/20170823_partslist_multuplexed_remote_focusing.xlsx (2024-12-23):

Category | Purpose | Vendor | Part Number | Item | Product URL | Qty | Price | Subtotal | Currency | Order? | Arrived? | Comments
MuST | Beam path modifications | Thorlabs | LJ1695RM-B | f = 50 mm, Ø1", N-BK7 Mounted Plano-Convex Round Cyl Lens, ARC: 650 - 1050 nm | https://www.thorlabs.com/thorproduct.cfm?partnumber=LJ1695RM-B | 1 | $101.00 | $101.00 | USD
MuST | Beam path modifications | Thorlabs | LJ1653RM-B | f = 200 mm, Ø1", N-BK7 Mounted Plano-Convex Round Cyl Lens, ARC: 650 - 1050 nm | https://www.thorlabs.com/thorproduct.cfm?partnumber=LJ1653RM-B | 1 | $106.00 | $106.00 | USD
MuST | Beam path modifications | Thorlabs | AC254-060-B-ML | f=60mm, Ø1" Achromatic Doublet, SM1-Threaded Mount, ARC: 650-1050 nm | https://www.thorlabs.com/thorproduct.cfm?partnumber=AC254-060-B-ML | 1 | $111.00 | $111.00 | USD
MuST | Beam path modifications | Thorlabs | LB1945-B-ML | Mounted N-BK7 Bi-Convex Lens, Ø1", f = 200.0 mm, ARC: 650-1050 nm | https://www.thorlabs.com/thorproduct.cfm?partnumber=LB1945-B-ML | 1 | $44.25 | $44.25 | USD
MuST | Beam path modifications | Thorlabs | LB1437-B-ML | Mounted N-BK7 Bi-Convex Lens, Ø1", f = 150.0 mm, ARC: 650-1050 nm | https://www.thorlabs.com/thorproduct.cfm?partnumber=LB1437-B-ML | 1 | $44.50 | $44.50 | USD
MuST | Beam path modifications | Thorlabs | LB1901-B-ML | Mounted N-BK7 Bi-Convex Lens, Ø1", f = 75.0 mm, ARC: 650-1050 nm | https://www.thorlabs.com/thorproduct.cfm?partnumber=LB1901-B-ML | 1 | $45.75 | $45.75 | USD
MuST | Beam path modifications | Thorlabs | LB1676-B-ML | Mounted N-BK7 Bi-Convex Lens, Ø1", f = 100.0 mm, ARC: 650-1050 nm | https://www.thorlabs.com/thorproduct.cfm?partnumber=LB1676-B-ML | 1 | $45.00 | $45.00 | USD
MuST | Beam path modifications | Thorlabs | LJ1728L1-B | f = 50.80 mm, H = 50.80 mm, L = 53.0 mm, N-BK7 Plano-Convex Cylindrical Lens, Antireflection Coating: 650-1050 nm | https://www.thorlabs.com/thorproduct.cfm?partnumber=LJ1728L1-B | 1 | $175.00 | $175.00 | USD
MuST | Beam path modifications | CVI Melles Griot | SCX-50.8-76.3-UV-1030 | SCX-UV: Laser Quality Fused Silica Square Plano-Convex Cylindrica Lenses | https://www.cvilaseroptics.com/scx-uv%3A-laser-quality-fused-silica-square-plano-convex-cylindrica-lenses/product/scx-uv_laser_quality_fused_silica_square_pla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 | 1 | $732.00 | $732.00 | USD
MuST | Beam path modifications | CVI Melles Griot | SCX-50.8-203.4-UV-1030 | SCX-UV: Laser Quality Fused Silica Square Plano-Convex Cylindrica Lenses | https://www.cvilaseroptics.com/scx-uv%3A-laser-quality-fused-silica-square-plano-convex-cylindrica-lenses/product/scx-uv_laser_quality_fused_silica_square_pla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 | 1 | $732.00 | $732.00 | USD
MuST | Beam path modifications | Thorlabs | LJ1996L1-B | f = 300.00 mm, H = 60.00 mm, L = 62.0 mm, N-BK7 Plano-Convex Cylindrical Lens, Antireflection Coating: 650-1050 nm | https://www.thorlabs.com/thorproduct.cfm?partnumber=LJ1996L1-B | 1 | $196.00 | $196.00 | USD
MuST | Beam path modifications | Edmund | #88-598-INK | 75mm Dia. x 400mm FL, VIS-NIR, Inked, Achromatic Lens | https://www.edmundoptics.com/optics/optical-lenses/achromatic-lenses/vis-nir-coated-achromatic-lenses/88598INK/ | 1 | $284.00 | $284.00 | USD
MuST | Beam path modifications | Thorlabs | LMR3/M | Lens Mount with Retaining Ring for Ø3" Optics, M4 Tap | https://www.thorlabs.com/thorproduct.cfm?partnumber=LMR3/M | 1 | $52.50 | $52.50 | USD
MuST | Beam path modifications | Thorlabs | CH2B | Fixed Cylindrical Lens Mount, Max Optic Height: 2.60" (66.0 mm) | https://www.thorlabs.com/thorproduct.cfm?partnumber=CH2B | 4 | $65.25 | $261.00 | USD
MuST | Remote focussing | Edmund | #48-881 | 12.5mm 980nm, Laser Line Polarizing Cube Beamsplitter | https://www.edmundoptics.com/optics/beamsplitters/cube-beamsplitters/12.5mm-980nm-laser-line-polarizing-cube-beamsplitter/ | 1 | $100.00 | $100.00 | USD
MuST | Remote focussing | Thorlabs | AQWP05M-980 | Ø1/2" Mounted Achromatic Quarter-Wave Plate, Ø1" Mount, 690 - 1200 nm | https://www.thorlabs.com/thorproduct.cfm?partnumber=AQWP05M-980 | 1 | $799.00 | $799.00 | USD
MuST | Remote focussing | Thorlabs | PRM1 | High-Precision Rotation Mount for Ø1" (25.4 mm) Optics | https://www.thorlabs.com/thorproduct.cfm?partnumber=PRM1 | 1 | $274.00 | $274.00 | USD
MuST | 4x multiplexing | Thorlabs | KM100DL | Left-Handed Kinematic Mount for Ø1" D-Shaped Mirrors | https://www.thorlabs.com/thorproduct.cfm?partnumber=KM100DL | 2 | $77.25 | $154.50 | USD
MuST | 4x multiplexing | Thorlabs | DMM1/M | Fixed Mount for Ø1" D-Shaped Mirrors, Metric | https://www.thorlabs.com/thorproduct.cfm?partnumber=DMM1/M | 2 | $61.50 | $123.00 | USD

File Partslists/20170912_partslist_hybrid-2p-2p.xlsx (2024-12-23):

Category | Purpose | Vendor | Part Number | Item | Product URL | Qty | Price | Subtotal | Currency | Order? | Arrived? | Comments
Hybrid-MuST | 3p scan relay | Thorlabs | LB1904-C-ML | Mounted N-BK7 Bi-Convex Lens, Ø1", f = 125.0 mm, ARC: 1050 - 1700 nm | https://www.thorlabs.com/thorproduct.cfm?partnumber=LB1904-C-ML | 2 | $48.25 | $96.50 | USD
Hybrid-MuST | Beam path modifications | Thorlabs | ER8-P4 | Cage Assembly Rod, 8" Long, Ø6 mm, 4 Pack | https://www.thorlabs.com/thorproduct.cfm?partnumber=ER8-P4 | 2 | $44.60 | $89.20 | USD
Hybrid-MuST | Beam path modifications | Thorlabs | ER4-P4 | Cage Assembly Rod, 4" Long, Ø6 mm, 4 Pack | https://www.thorlabs.com/thorproduct.cfm?partnumber=ER4-P4 | 2 | $26.98 | $53.96 | USD
Hybrid-MuST | Beam path modifications | Thorlabs | CP02T/M | SM1-Threaded 30 mm Cage Plate, 0.50" Thick, 2 Retaining Rings, M4 Tap | https://www.thorlabs.com/thorproduct.cfm?partnumber=CP02T/M | 5 | $21.50 | $107.50 | USD
Hybrid-MuST | Beam path modifications | Thorlabs | VRC4CPT | 30 mm Cage System Alignment Plate with IR Disk (790 - 840 nm, 870 - 1070 nm, 1500 - 1590 nm) | https://www.thorlabs.com/thorproduct.cfm?partnumber=VRC4CPT#ad-image-0 | 1 | $30.25 | $30.25 | USD
Hybrid-MuST | Beam path modifications | Thorlabs | KM100C | Kinematic Mount for up to 1.3" (33 mm) Tall Rectangular Optics, Right Handed | https://www.thorlabs.com/thorproduct.cfm?partnumber=KM100C | 1 | $94.75 | $94.75 | USD
Hybrid-MuST | Beam path modifications | Thorlabs | PFSQ20-03-P01 | 2" x 2" Protected Silver Mirror, 6.0 mm Thick | https://www.thorlabs.com/thorproduct.cfm?partnumber=PFSQ20-03-P01 | 3 | $114.00 | $342.00 | USD
Hybrid-MuST | Beam path modifications | Thorlabs | KM200S | Kinematic Mount for 2" (50.8 mm) Tall Rectangular Optics, Right Handed | https://www.thorlabs.com/thorproduct.cfm?partnumber=KM200S | 3 | $136.00 | $408.00 | USD
Hybrid-MuST | Beam path modifications | Thorlabs | TR20/M-P5 | Ø12.7 mm Optical Post, SS, M4 Setscrew, M6 Tap, L = 20 mm, 5 Pack | https://www.thorlabs.com/thorproduct.cfm?partnumber=TR20/M-P5 | 1 | $21.33 | $21.33 | USD
Hybrid-MuST | Beam path modifications | Thorlabs | PH20/M-P5 | Ø12.7 mm Post Holder, Spring-Loaded Hex-Locking Thumbscrew, L=20 mm, 5 Pack | https://www.thorlabs.com/thorproduct.cfm?partnumber=PH20/M-P5#ad-image-0 | 1 | $35.15 | $35.15 | USD
Hybrid-MuST | Beam path modifications | Thorlabs | BE1/M-P5 | Ø31.8 mm Studded Pedestal Base Adapter, M6 Thread, 5 Pack | https://www.thorlabs.com/thorproduct.cfm?partnumber=BE1/M-P5 | 1 | $46.50 | $46.50 | USD
Hybrid-MuST | Beam path modifications | Thorlabs | CF125C/M-P5 | Clamping Fork, 31.5 mm Counterbored Slot, M6 x 1.0 Captive Screw, 5 Pack | https://www.thorlabs.com/thorproduct.cfm?partnumber=CF125C/M-P5 | 1 | $51.43 | $51.43 | USD
Hybrid-MuST | Beam path modifications | Thorlabs | CF038C/M-P5 | Clamping Fork, 9.5 mm Counterbored Slot, M6 x 1.0 Captive Screw, 5 Pack | https://www.thorlabs.com/thorproduct.cfm?partnumber=CF038C/M-P5 | 1 | $47.25 | $47.25 | USD
Hybrid-MuST | Polarization adjustment | Thorlabs | AHWP05M-980 | Ø1/2" Mounted Achromatic Half-Wave Plate, Ø1" Mount, 690 - 1200 nm | https://www.thorlabs.com/thorproduct.cfm?partnumber=AHWP05M-980 | 2 | $799.00 | $1598.00 | USD
Hybrid-MuST | Polarization adjustment | Thorlabs | RSP1/M | Rotation Mount for Ø1" (25.4 mm) Optics, M4 Tap | https://www.thorlabs.com/thorproduct.cfm?partnumber=RSP1/M#ad-image-0 | 2 | $84.50 | $169.00 | USD
Hybrid-MuST | Beam path modifications | Thorlabs | UM10-AG | Ø1" Ultrafast-Enhanced Silver Mirror, 750 - 1000 nm | https://www.thorlabs.com/thorproduct.cfm?partnumber=UM10-AG | 5 | $97.00 | $485.00 | USD
Hybrid-MuST | Supply | McMaster | 91292A441 | 18-8 Stainless Steel Socket Head Screw, M6 x 1 mm Thread, 10 mm Long | https://www.mcmaster.com/#91292a441/=196na32 | 1 | $6.03 | $6.03 | USD
Hybrid-MuST | Supply | McMaster | 91292A134 | 18-8 Stainless Steel Socket Head Screw, M6 x 1 mm Thread, 12 mm Long | https://www.mcmaster.com/#91292a134/=196nac0 | 1 | $7.22 | $7.22 | USD
Hybrid-MuST | Supply | McMaster | 93475A250 | 18-8 Stainless Steel Washer for M6 Screw Size, 6.4 mm ID, 12 mm OD | https://www.mcmaster.com/#93475a250/=196naqo | 1 | $4.86 | $4.86 | USD
Hybrid-MuST | Separate animal from optics | Thorlabs | TPS6 | 24" x 12" (610 mm x 305 mm) Straight Laser Safety Screen | https://www.thorlabs.com/newgrouppage9.cfm?objectgroup_id=6413 | 1 | $93.75 | $93.75 | USD

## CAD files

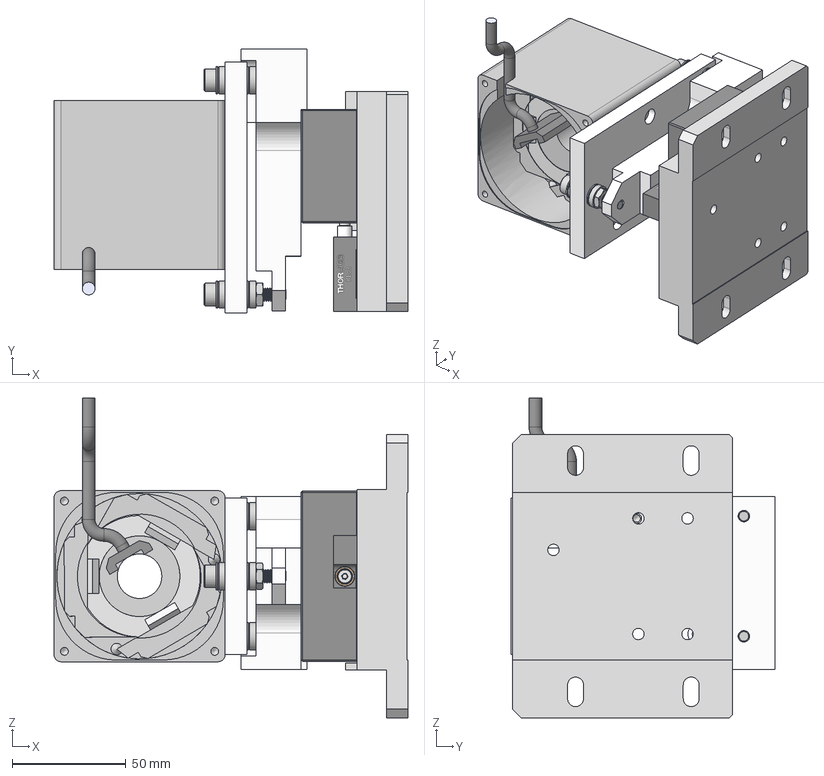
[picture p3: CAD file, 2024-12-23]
Mechanical/11_custom_remote-focusing-voicecoil-mount/LFA mount assembly v17.step
155.5 x 115.8 x 140.5 mm
base
bobbin
arm x 6
bobbin (1)
LFA_mount_top
94007A030_TYPE 18-8 STAINLESS STEEL ALIGNMENT WASHER x 6
91292A139_TYPE 18-8 SS SOCKET HEAD CAP SCREW x 5
90710A038_TYPE 18-8 SS THIN HEX NUT - DIN 439B
LFA_mount_bottom
BA2S7_M-Step
RFMirrBase
KL02-Step

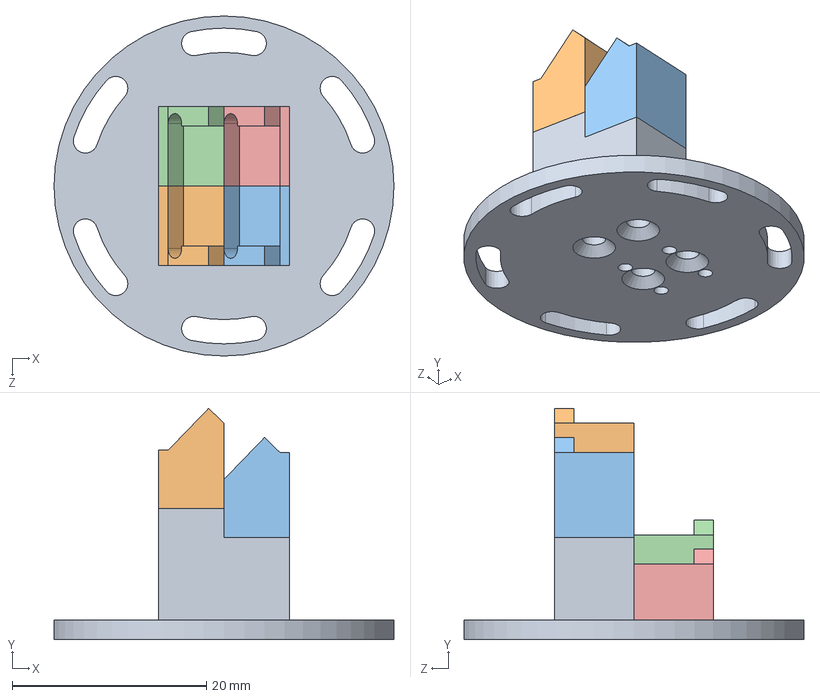
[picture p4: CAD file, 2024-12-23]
Mechanical/14_custom_tefo-4x-grating-holder/Grating Assembly V3 MPFI.SLDASM
35.0 x 23.8 x 35.0 mm
Grating Device V3 MPFI
Grating Devise V3 Insert 1 MPFI
Grating Devise V3 Insert 2 MPFI
Grating Devise V3 Insert 3 MPFI
Grating Devise V3 Insert 4 MPFI

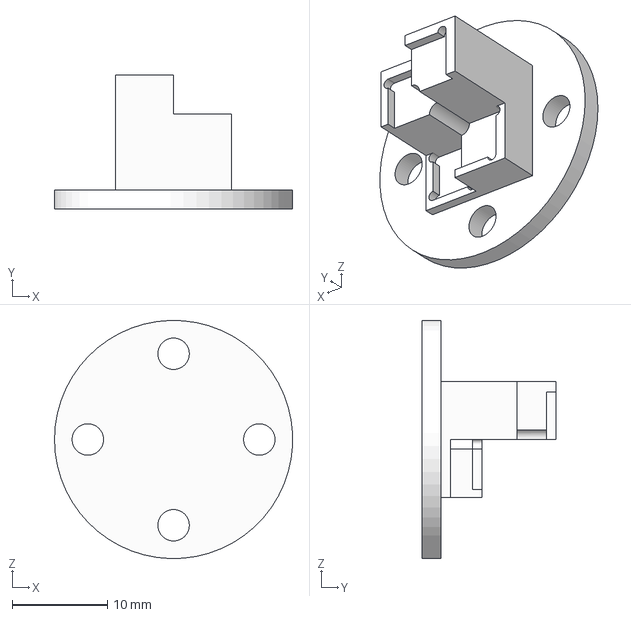
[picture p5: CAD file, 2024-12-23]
Mechanical/11_custom_remote-focusing-voicecoil-mount/Mirror holder/Mirror holder for VC v8.step
25.0 x 14.1 x 25.0 mm

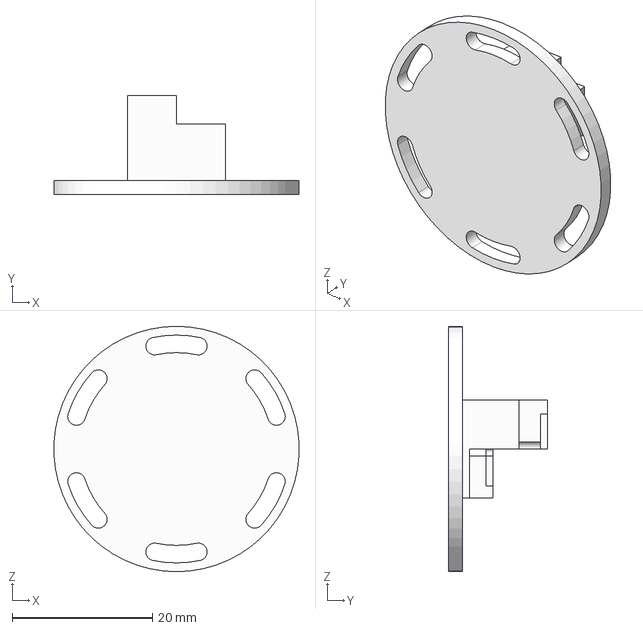
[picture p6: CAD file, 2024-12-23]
Mechanical/11_custom_remote-focusing-voicecoil-mount/Mirror holder/wrong bobbin/Mirror holder for VC v4.step
34.9 x 14.1 x 35.0 mm

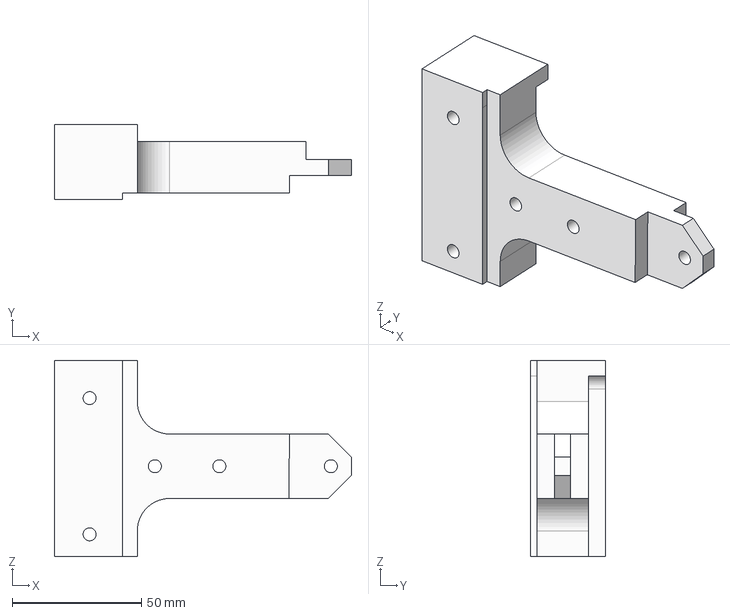
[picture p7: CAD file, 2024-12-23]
Mechanical/11_custom_remote-focusing-voicecoil-mount/Mount/LFA_mount_bottom v11.step
115.1 x 29.0 x 76.0 mm

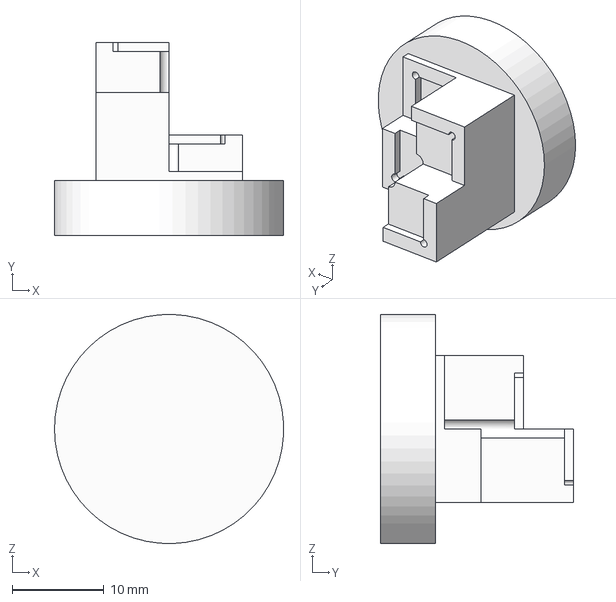
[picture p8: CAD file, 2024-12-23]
Mechanical/12_custom_4x-mirror-holder_voicecoil-remote-focusing/Mirror holder -v3 v3.step
25.0 x 21.1 x 25.0 mm

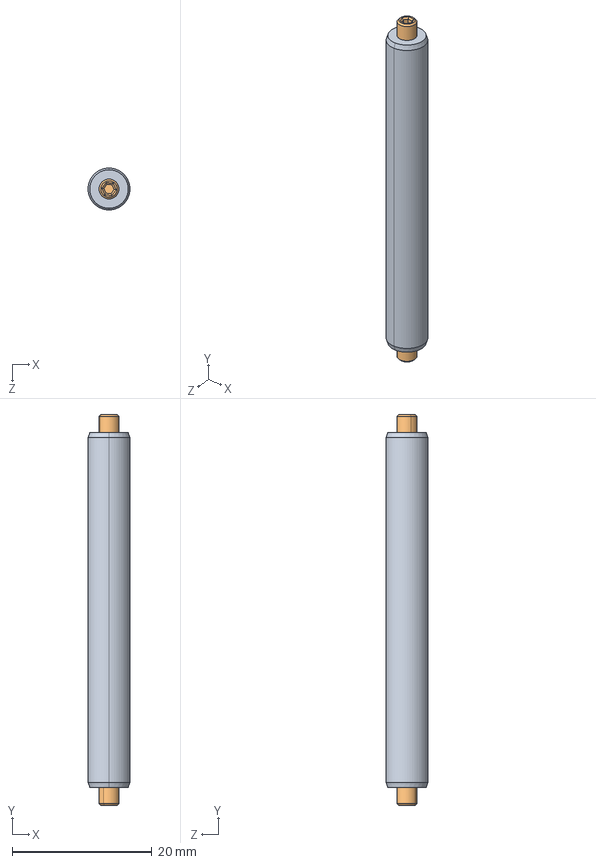
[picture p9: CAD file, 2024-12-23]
Mechanical/13_custom_alternative_adjustable-4x-mirror-holder/ER2-Step.step
5.99 x 55.9 x 5.99 mm

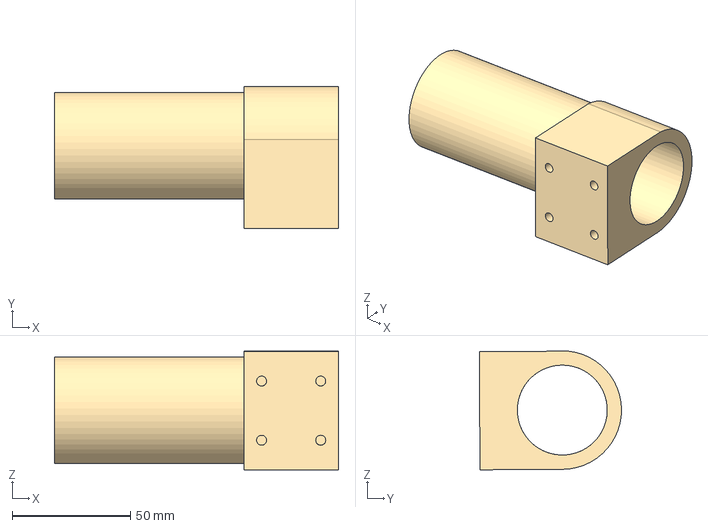
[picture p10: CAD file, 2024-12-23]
Mechanical/20_customized_Sutter-MOM285/element02 v8.step
120.0 x 60.0 x 50.1 mm

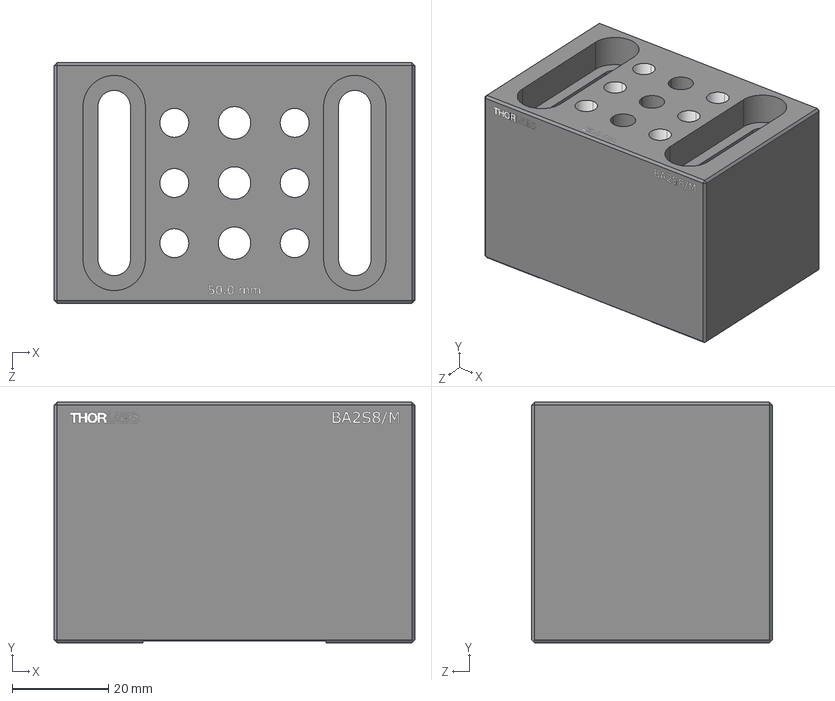
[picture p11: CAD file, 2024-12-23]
Mechanical/11_custom_remote-focusing-voicecoil-mount/BA2S8_M-Step.step
75.0 x 50.0 x 50.0 mm

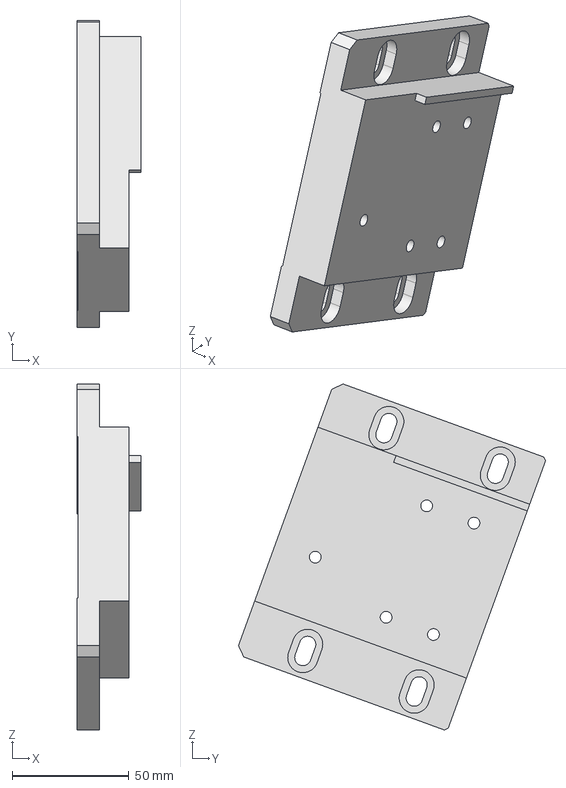
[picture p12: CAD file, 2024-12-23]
Mechanical/11_custom_remote-focusing-voicecoil-mount/Mount/RFMirrBase v3.step
27.4 x 131.6 x 148.2 mm

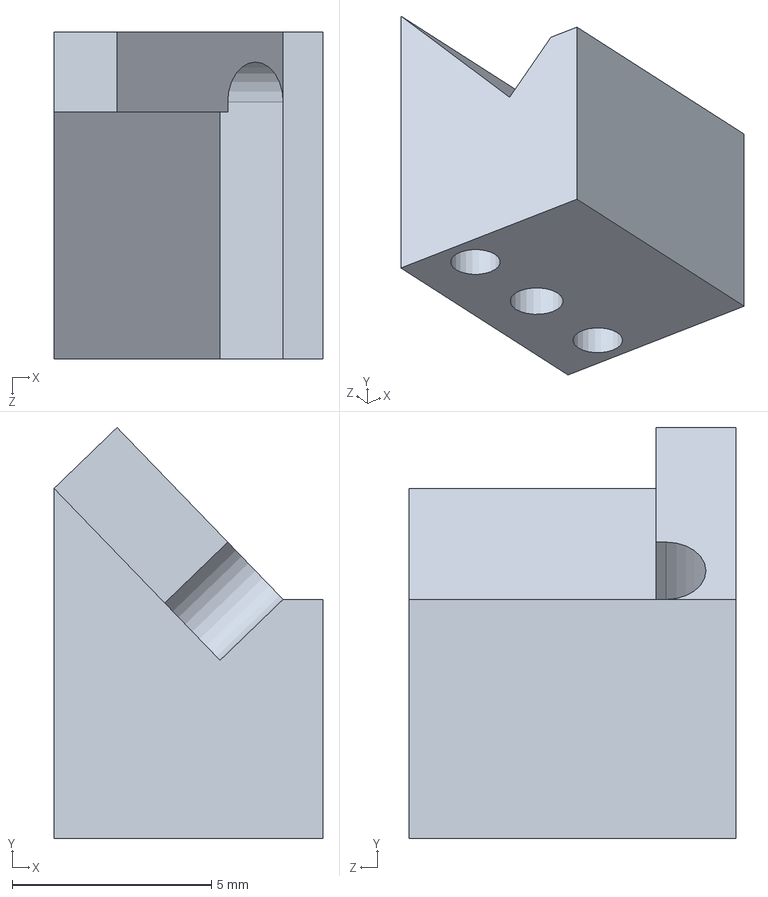
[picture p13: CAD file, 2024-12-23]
Mechanical/14_custom_tefo-4x-grating-holder/Grating Devise V3 Insert 1 MPFI.SLDPRT
6.75 x 10.3 x 8.20 mm

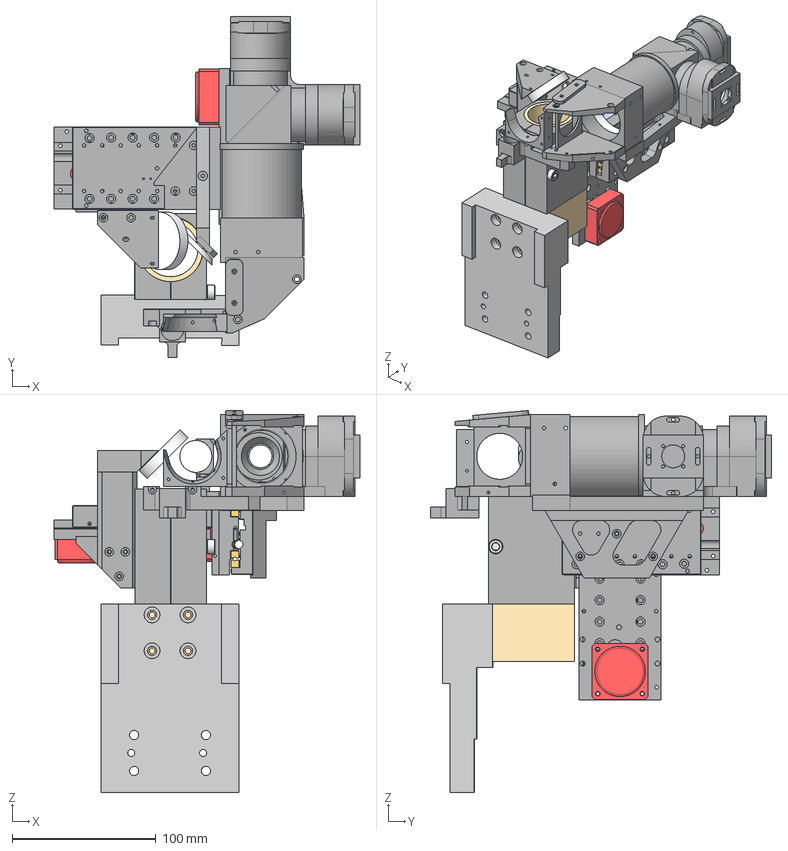
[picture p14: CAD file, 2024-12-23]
Mechanical/20_customized_Sutter-MOM285/Denk 2P Current For Janelia Path v3.step
212.8 x 237.3 x 265.9 mm
element01 v5
element02 v7
91292A144
Mounting bracket v1

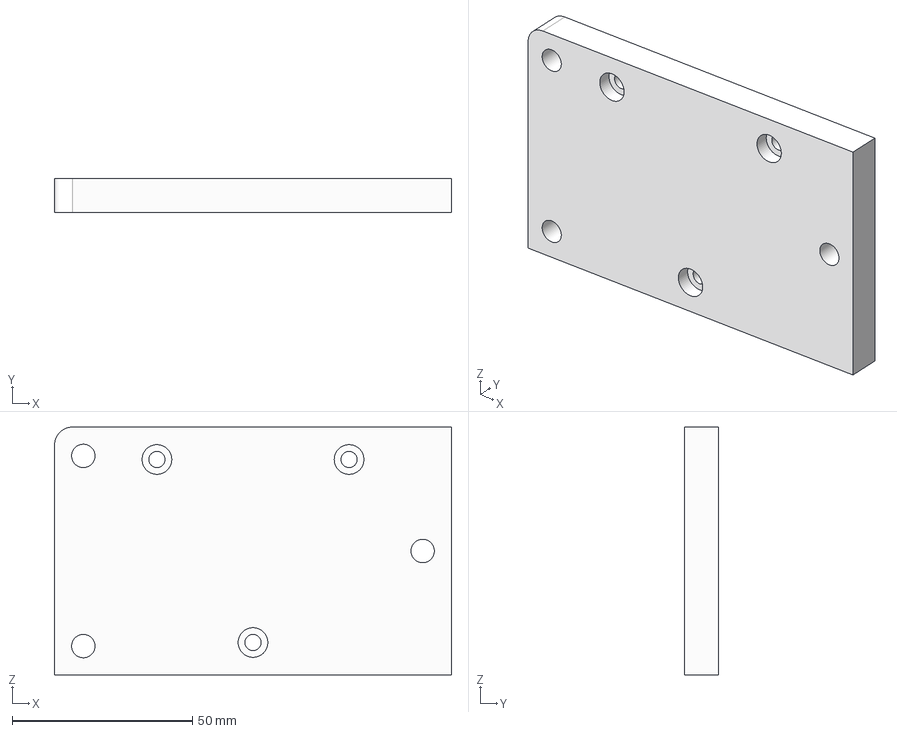
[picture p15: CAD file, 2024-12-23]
Mechanical/11_custom_remote-focusing-voicecoil-mount/Mount/LFA_mount_top v6.step
110.2 x 9.50 x 68.8 mm

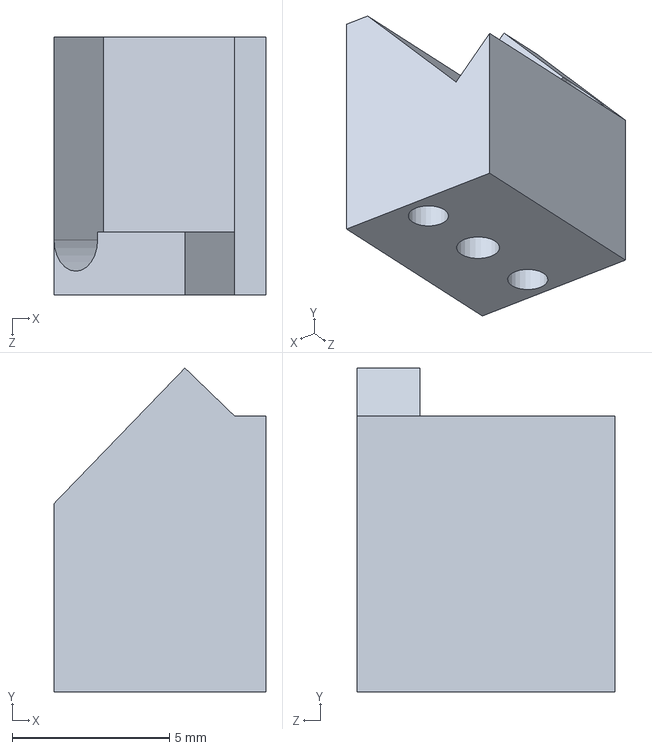
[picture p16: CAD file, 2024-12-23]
Mechanical/14_custom_tefo-4x-grating-holder/Grating Devise V3 Insert 2 MPFI.SLDPRT
6.75 x 10.3 x 8.20 mm

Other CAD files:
Mechanical/11_custom_remote-focusing-voicecoil-mount/RFMirrBase.step
Mechanical/20_customized_Sutter-MOM285/element01 v5.step
Mechanical/14_custom_tefo-4x-grating-holder/Grating Devise V3 Insert 3 MPFI.SLDPRT
Mechanical/14_custom_tefo-4x-grating-holder/Grating Devise V3 Insert 4 MPFI.SLDPRT
Mechanical/10_custom_tefo-2x-grating-holder/90895A005_TYPE 18-8 SS BELLEVILLE SPRING LOCK WASHER.STEP
Mechanical/10_custom_tefo-2x-grating-holder/91292A111_TYPE 18-8 SS SOCKET HEAD CAP SCREW.STEP
Mechanical/10_custom_tefo-2x-grating-holder/91292A801_TYPE 18-8 SS SOCKET HEAD CAP SCREW.STEP
Mechanical/10_custom_tefo-2x-grating-holder/91828A211_TYPE 18-8 STAINLESS STEEL HEX NUT.STEP
Mechanical/10_custom_tefo-2x-grating-holder/9714K220_WAVE DISC SPRING.STEP
Mechanical/11_custom_remote-focusing-voicecoil-mount/90710A038_TYPE 18-8 SS THIN HEX NUT - DIN 439B.STEP
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

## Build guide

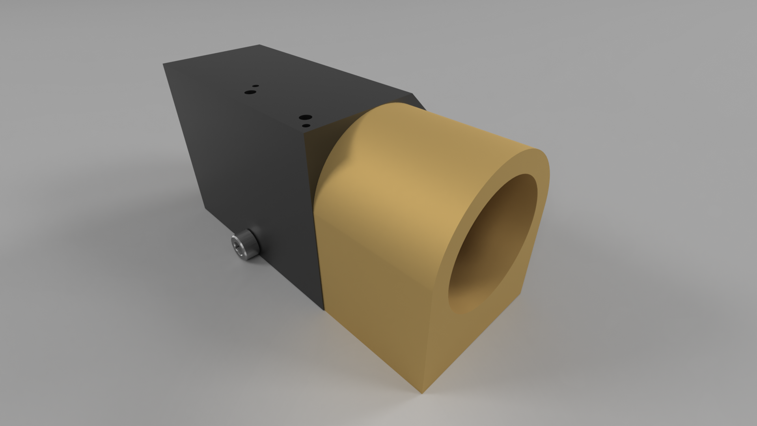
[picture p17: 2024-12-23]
Mechanical/20_customized_Sutter-MOM285/Assembly_2017-Mar-08_03-30-31PM-000_CustomizedView41992969737.png

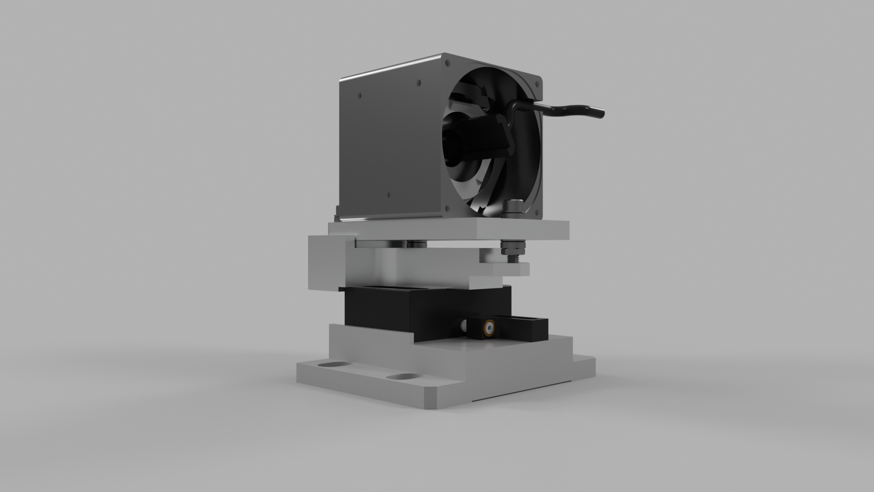
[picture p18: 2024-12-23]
Mechanical/11_custom_remote-focusing-voicecoil-mount/LFA_mount_assembly_2018-Jan-20_12-15-59AM-000_CustomizedView17901469473_png.png

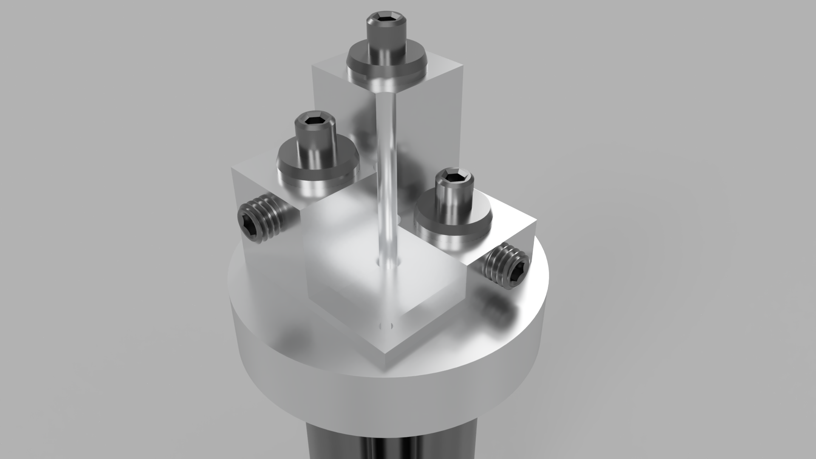
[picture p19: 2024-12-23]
Mechanical/13_custom_alternative_adjustable-4x-mirror-holder/Mirror_holder_assembly_2018-May-09_05-59-09PM-000_CustomizedView39473900056_png.png

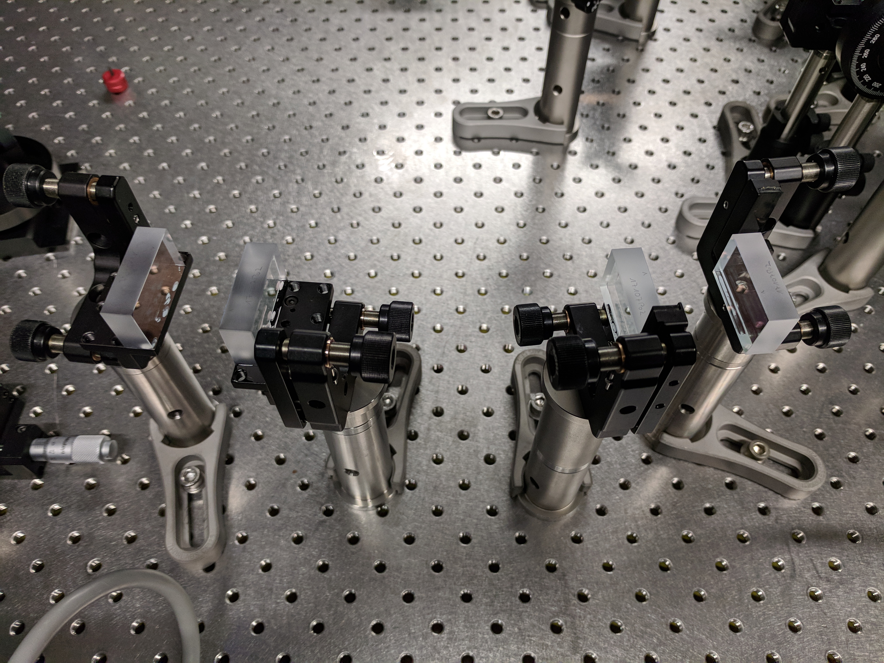
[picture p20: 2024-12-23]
Docs_Photos/HyMS_setup_photos/IMG_20171208_171709.jpg

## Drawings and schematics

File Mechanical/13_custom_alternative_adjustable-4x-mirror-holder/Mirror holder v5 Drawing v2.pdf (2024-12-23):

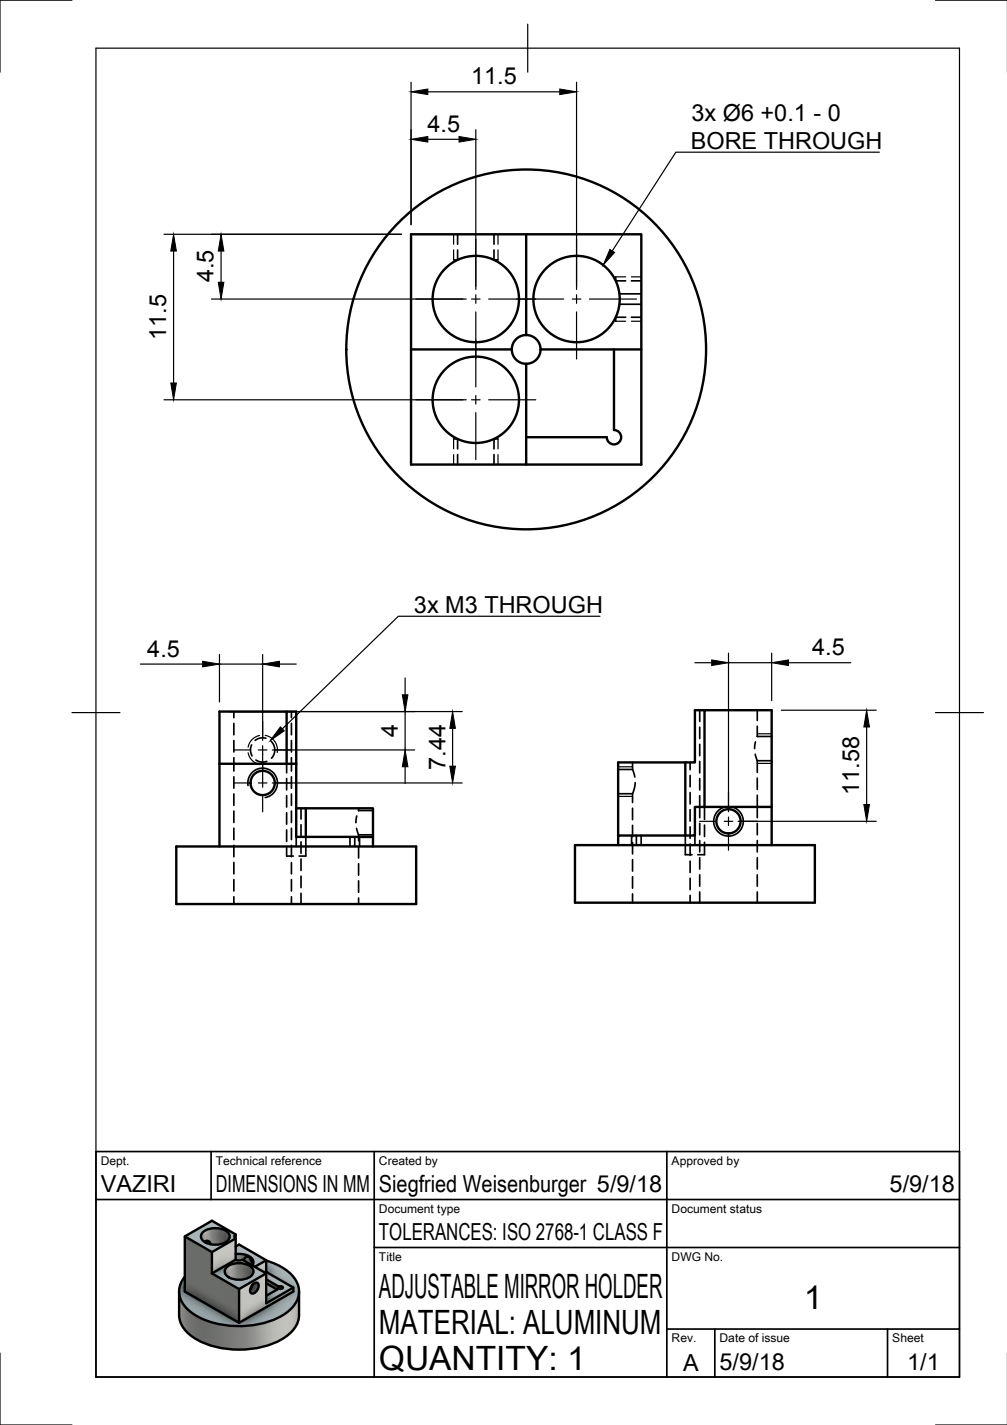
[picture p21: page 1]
VAZIRI; DIMENSIONS IN MM; Siegfried Weisenburger 4.5 11.5; BORE THROUGH; 3x M3 THROUGH

Dept. | Technical reference | Created by 5/9/18 | Approved by 5/9/18

Document type TOLERANCES: ISO 2768-1 CLASS F | Document status

Title MATERIAL: ALUMINUM QUANTITY: 1 | DWG No. 1 ADJUSTABLE MIRROR HOLDER

Rev. A | Date of issue 5/9/18 | Sheet 1/1

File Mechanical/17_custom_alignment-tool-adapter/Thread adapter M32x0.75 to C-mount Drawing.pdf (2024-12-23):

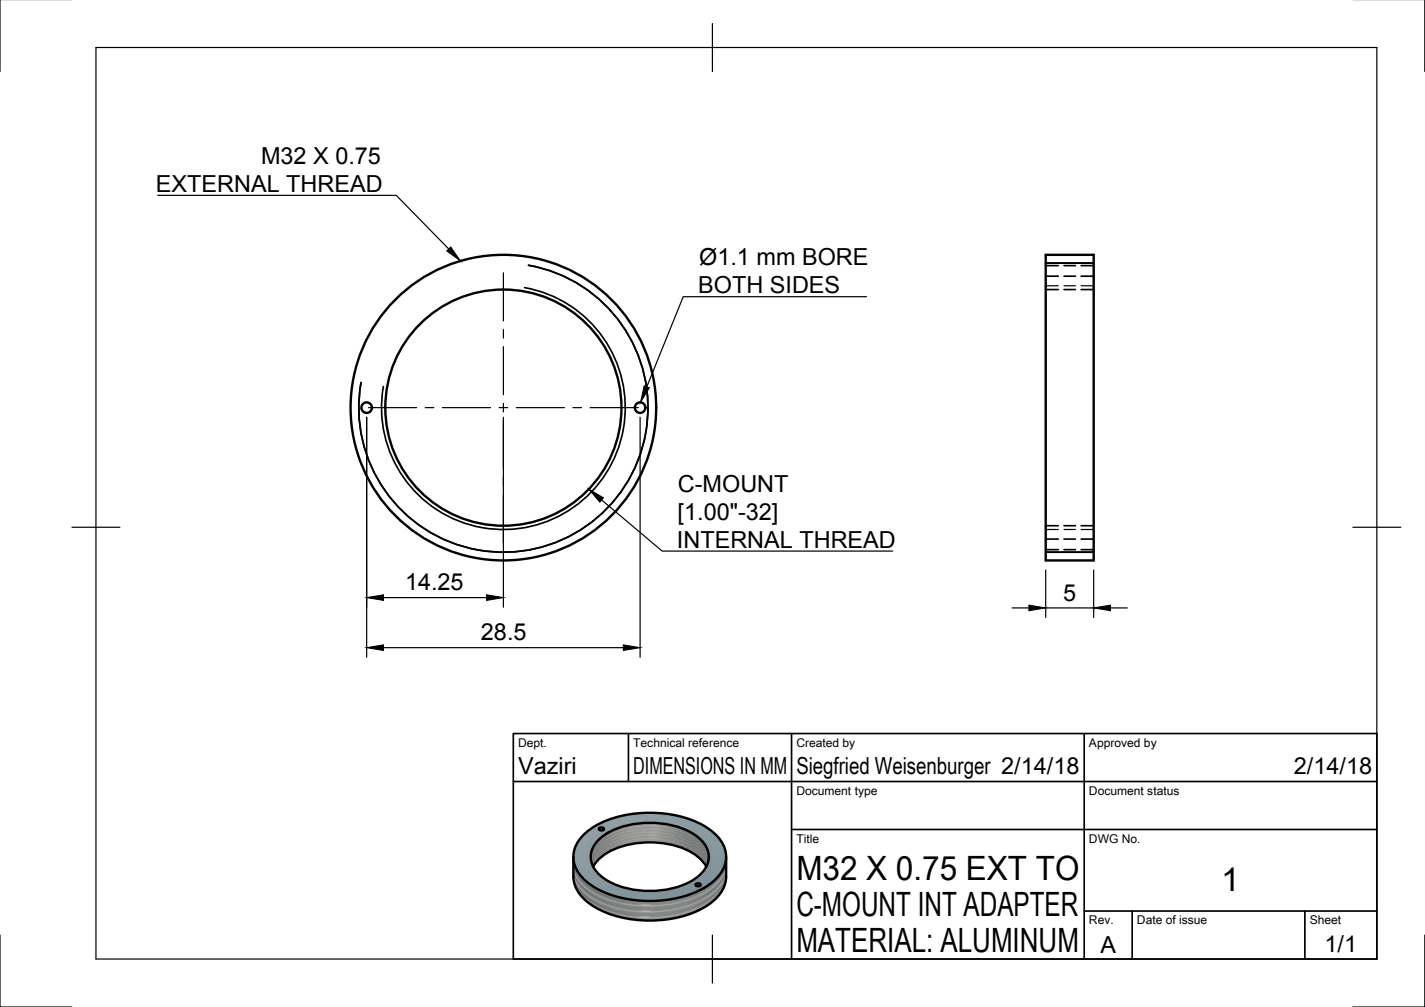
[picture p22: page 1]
Ø1.1 mm BORE BOTH SIDES; M32 X 0.75 EXTERNAL THREAD; INTERNAL THREAD

Dept. Vaziri | Technical reference DIMENSIONS IN MM | Created by Siegfried Weisenburger 2/14/18 | Approved by 2/14/18

Document type | Document status

Title M32 X 0.75 EXT TO C-MOUNT INT ADAPTER MATERIAL: ALUMINUM | DWG No. 1

Rev. A | Date of issue | Sheet 1/1

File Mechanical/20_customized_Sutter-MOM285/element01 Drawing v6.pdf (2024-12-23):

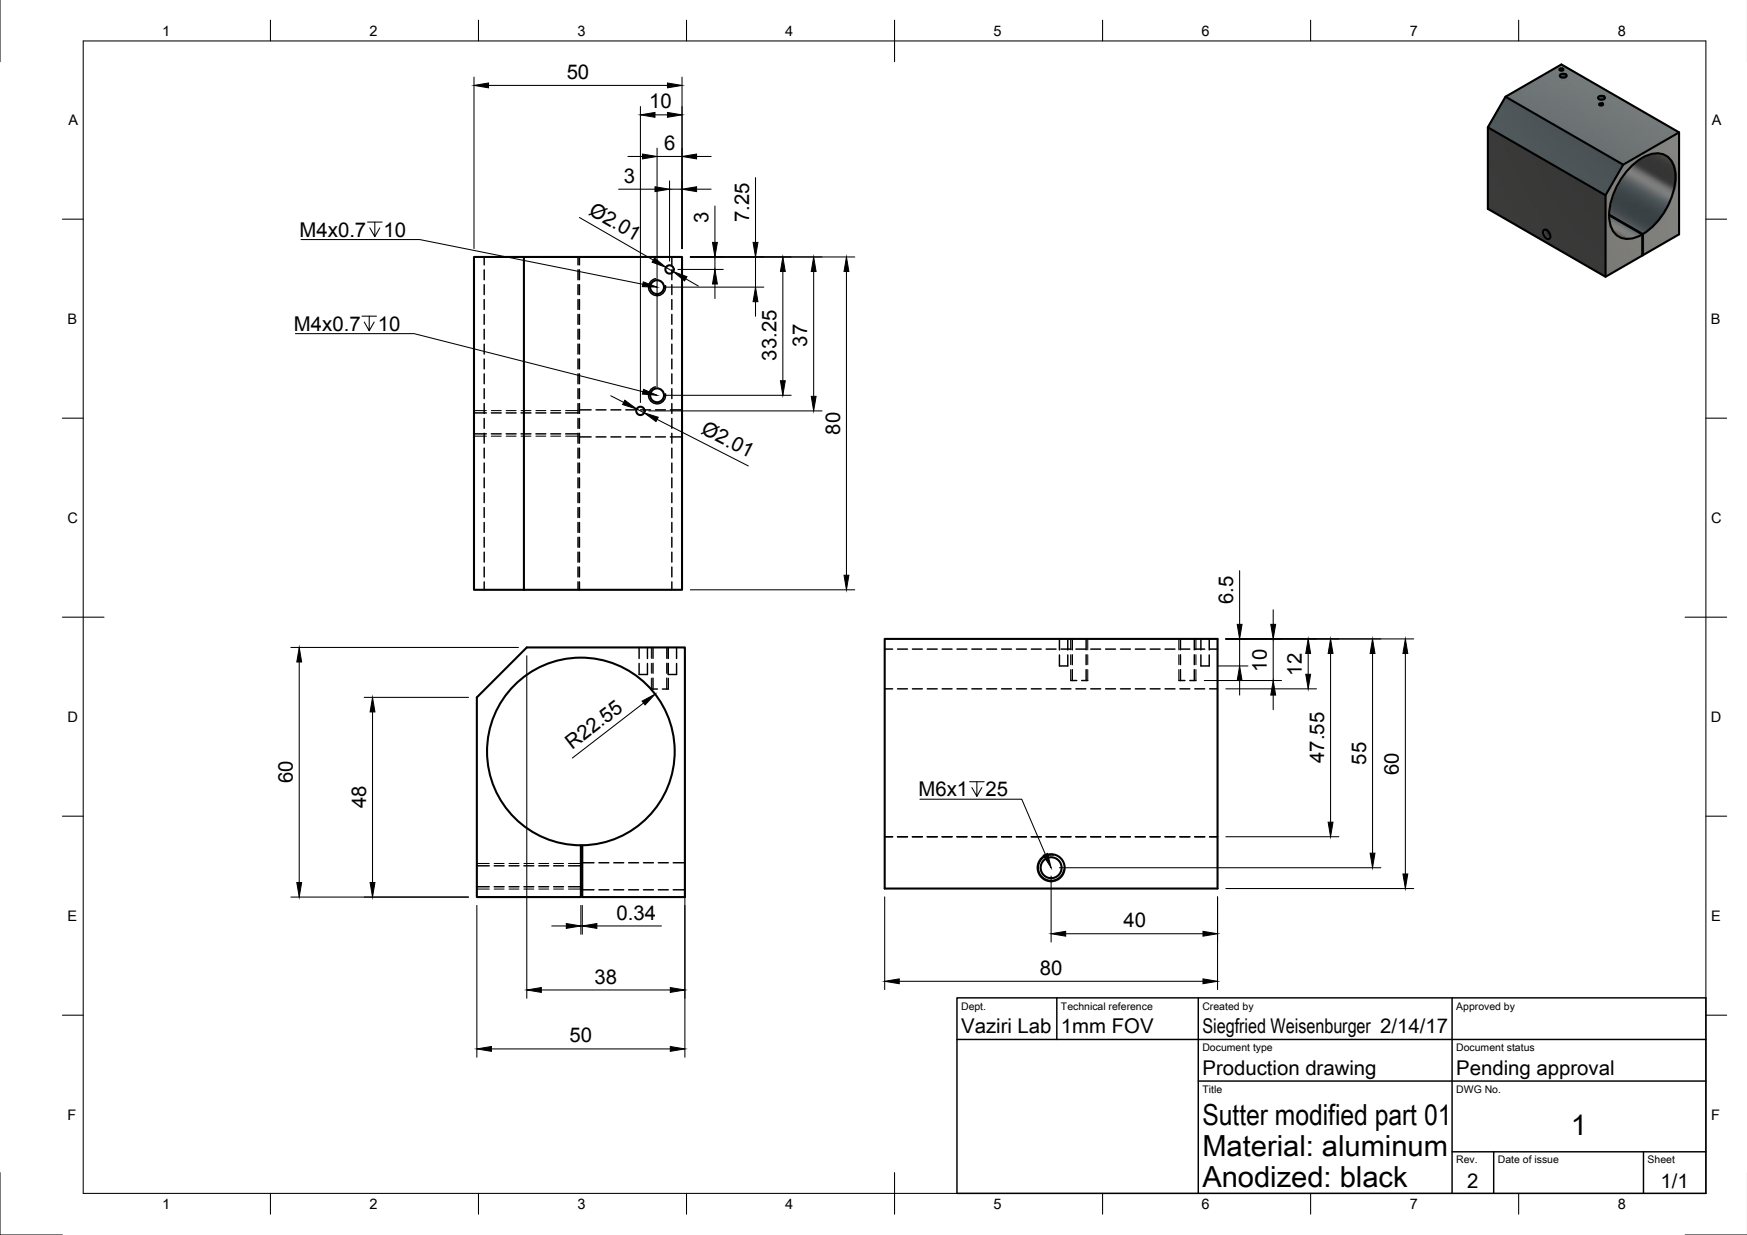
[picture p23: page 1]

Dept. Vaziri Lab | Technical reference 1mm FOV | Created by Siegfried Weisenburger 2/14/17 | Approved by

Document type Production drawing | Document status Pending approval

Title Material: aluminum Anodized: black | DWG No. 1 Sutter modified part 01

Rev. 2 | Date of issue | Sheet 1/1

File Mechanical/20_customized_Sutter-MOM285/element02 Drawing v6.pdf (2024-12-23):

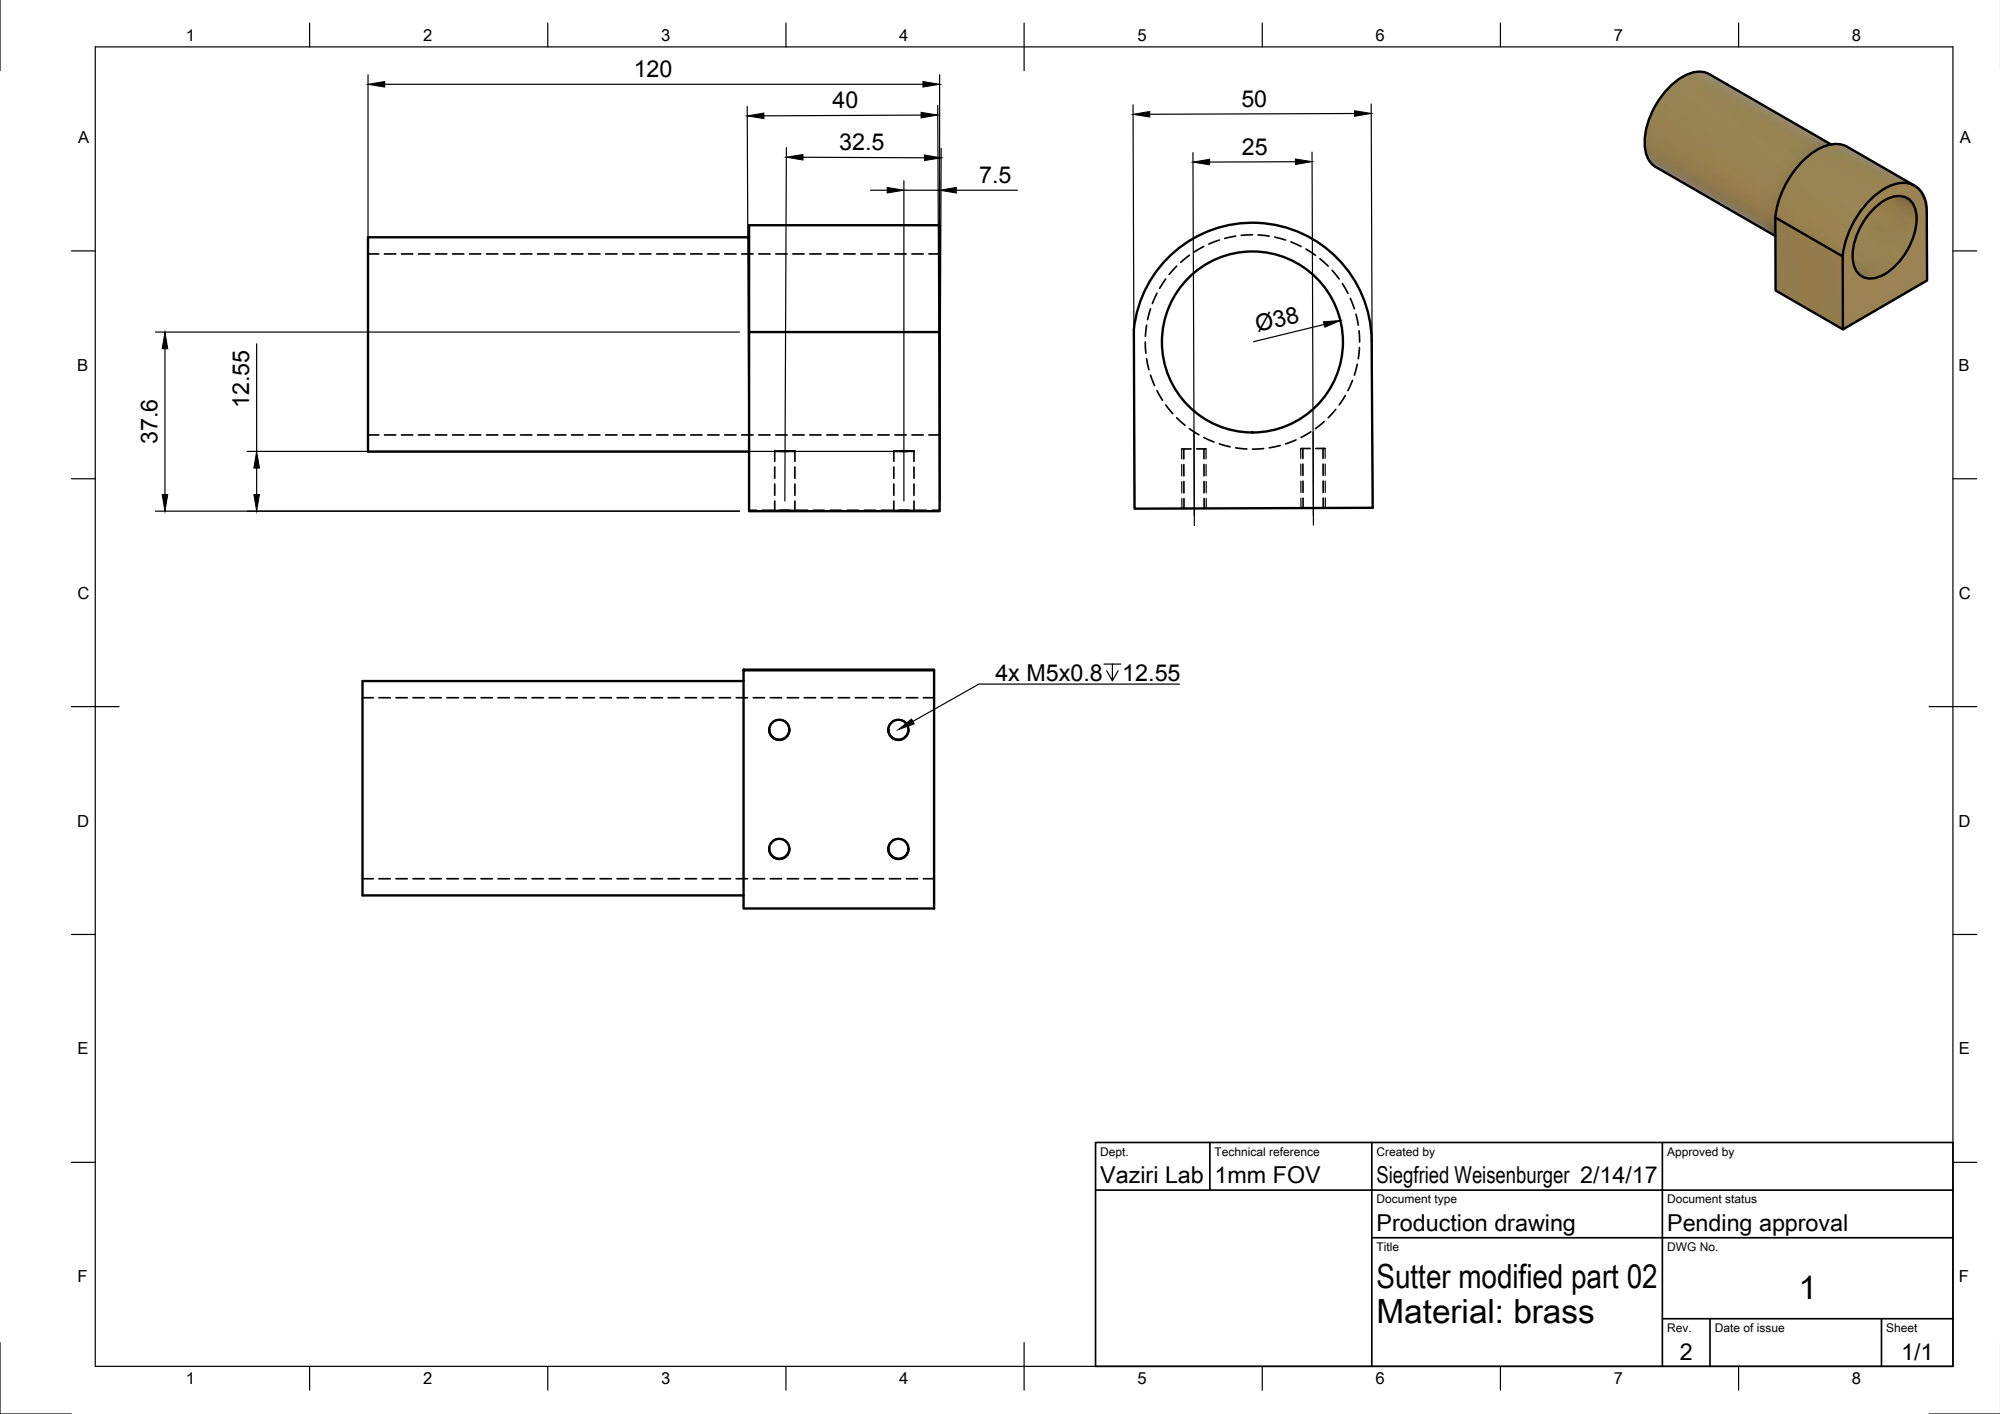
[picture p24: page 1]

Dept. Vaziri Lab | Technical reference 1mm FOV | Created by Siegfried Weisenburger 2/14/17 | Approved by

Document type Production drawing | Document status Pending approval

Title Material: brass | DWG No. 1 Sutter modified part 02

Rev. 2 | Date of issue | Sheet 1/1

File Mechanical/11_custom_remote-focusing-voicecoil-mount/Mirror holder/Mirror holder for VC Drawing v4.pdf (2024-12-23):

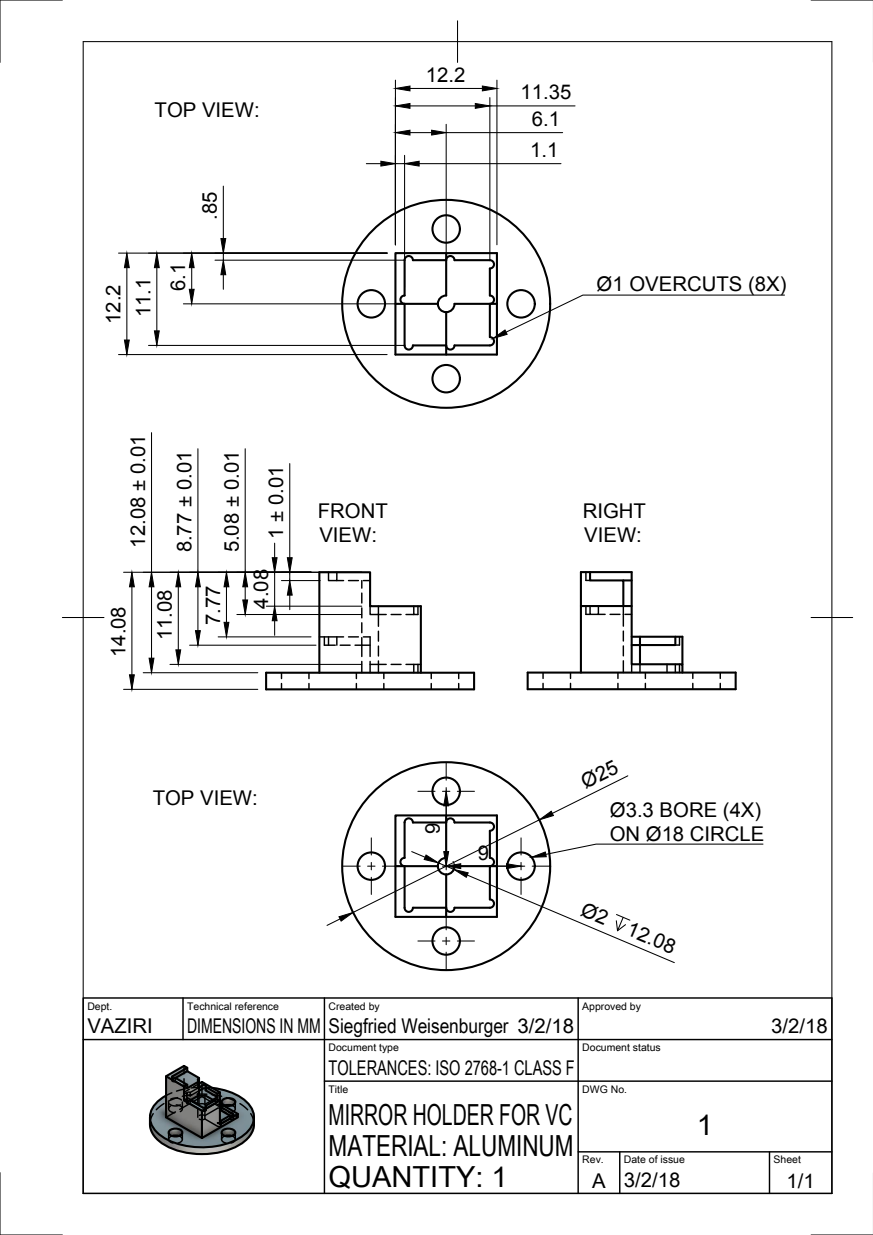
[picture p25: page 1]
Ø3.3 BORE (4X) ON Ø18 CIRCLE 9; Ø1 OVERCUTS (8X); TOP VIEW:

Dept. VAZIRI | Technical reference DIMENSIONS IN MM | Created by Siegfried Weisenburger 3/2/18 | Approved by 3/2/18

Document type TOLERANCES: ISO 2768-1 CLASS F | Document status

Title MIRROR HOLDER FOR VC MATERIAL: ALUMINUM QUANTITY: 1 | DWG No. 1

Rev. A | Date of issue 3/2/18 | Sheet 1/1

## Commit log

2024-12-23 Add mechanical, partslists, docs, photos
    [20161027_partslist-scantefo.xlsx, 20161129_partslist_multiplexing.xlsx, 20170329_partslist_3p.xlsx, 20170519_partslist_3p-beam-expander.xlsx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]
2025-01-13 Create 2019_partslist_3p_1mhz_microscope.xlsx
    Add parts list for 3p 1MHz microscope
    [2019_partslist_3p_1mhz_microscope.xlsx]
